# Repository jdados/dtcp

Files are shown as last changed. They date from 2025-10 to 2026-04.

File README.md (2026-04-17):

# CpE Design: DTCP Project Repository

## Overview

This repository presents the files associated with the design of a wireless neurostimulation platform powered through **Differential Tissue Coupled Powering (DTCP)**.  
The system transmits high-frequency (~20 – 25 MHz) differential signals through needle electrodes to power and communicate with implanted devices, while simultaneously recording **EMG (Electromyography)** activity for research.

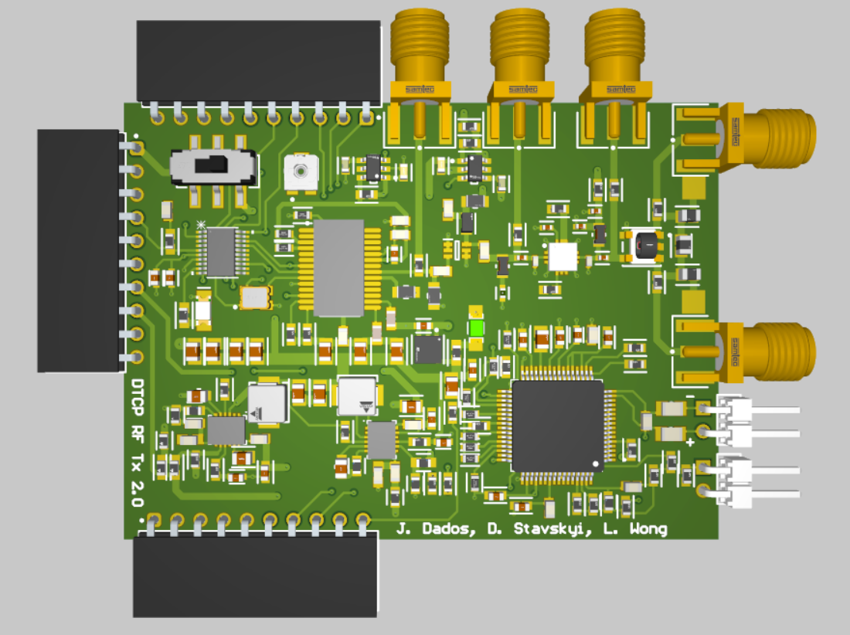
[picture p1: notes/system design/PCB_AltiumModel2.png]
Prototype 2 3D render


The project integrates four key subsystems:

1. **RF Signal Generation** – AD9850 DDS digitally tunes the HF output frequency.  
2. **Power Amplification** – 2 PAs in series deliver ≥ 1 W (≈ 30–35 dBm). Adjustable power through the help of a potentiometer and LED is included to make tuning power in surgery easier. It will light up when EMG signal is detected. 
3. **Signal Acquisition** – ADS1299 AFE captures and amplifies EMG signals.  
4. **Control & Interface** – MSPM0C1104 microcontroller manages DDS control, AFE sampling, and power switching.

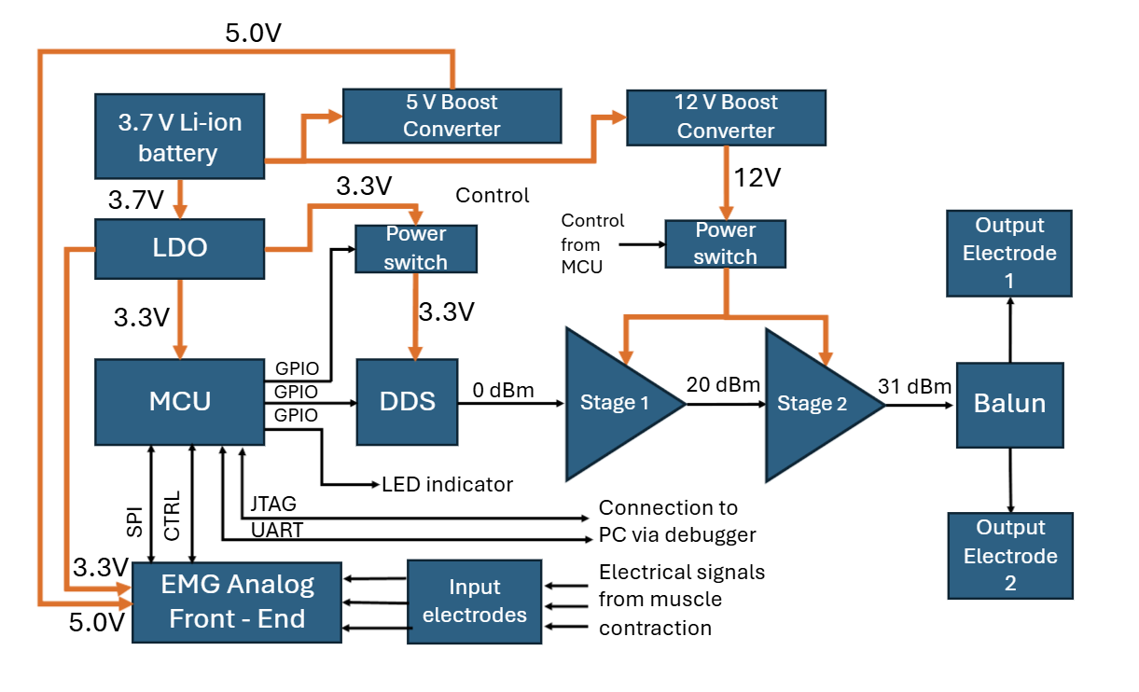
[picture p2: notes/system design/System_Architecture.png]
Prototype 2 System Architecture


## Project Plan

### **First Prototype**

The first prototype aims to realize the most basic functionality: a 25 MHz differential output at 1 W.

| Task | Finish By | Leader | Supporters | Comments | Status |
|------|------------|---------|-------------|-----------|---------|
| Design the PA circuit | End of October 2025 | Luis Wong | Jeremiah Dados |  | ✔️ |
| Design the EMG circuit | End of October 2025 | Dmytro Stavskyi | Jeremiah Dados |  | ✔️ |
| Design the first prototype PCB in Altium | Mid-November 2025 | Jeremiah Dados | Luis Wong, Dmytro Stavskyi |  | ✔️ |
| Place the fabrication order | Mid-November 2025 | Jeremiah Dados | Han Wu |  | ✔️ |
| Receive the board and assemble it | End of November 2025 | Jeremiah Dados | Luis Wong, Dmytro Stavskyi |  | ✔️ |
| Validate board outputs on lab equipment | Mid-December 2025 | Jeremiah Dados | Luis Wong, Dmytro Stavskyi | Present functional prototype at end of semester | ✔️ |
| Validate board functionality in animal experiments | End of January 2026 | Han Wu | Jeremiah Dados, Luis Wong, Dmytro Stavskyi | Work resumes 2nd week of January after winter break | 🟡 |

---

### **Second Prototype**

The second prototype addresses issues found in the first design and focuses on improving compactness, flexibility, and performance.

| Task | Finish By | Leader | Supporters | Comments | Status |
|------|------------|---------|-------------|-----------|---------|
| Revisions to the circuit design | Mid-February 2026 | Luis Wong, Dmytro Stavskyi | Jeremiah Dados |  | ✔️ |
| Design and order the PCB | End of February 2026 | Jeremiah Dados | Luis Wong, Dmytro Stavskyi |  | ✔️ |
| Place the fabrication order | End of February 2026 | Jeremiah Dados | Han Wu |  | ✔️ |
| Receive the board and assemble it | Mid-March 2026 | Luis Wong, Dmytro Stavskyi | Jeremiah Dados |  | ✔️ |
| Validate board outputs on lab equipment | End of March 2026 | Jeremiah Dados | Luis Wong, Dmytro Stavskyi |  | ✔️ |
| Validate board functionality in animal experiments | End of April 2026 | Han Wu | Jeremiah Dados, Luis Wong, Dmytro Stavskyi |  | 🟡 |

## Bugs

### Firmware

- `printf` is apparently too large to fit into the MCU, and debugging is harder without console printing
  - look for smaller alternative, UART cannot be used as it is utilized for EMG plotting through SerialPlot.
- Not yet sure if it causes or will cause problems, but the serial clock starts at high and remains high until the first transaction, even though it should be low when not transmitting or receiving data (and hence should start with low)
  - It has not seemed to though.
- Fluctuating offset, possibly due to noise from main, makes EMG detection algorithm non-trivial.

### Hardware

#### EMG Circuit

- Class A PA is part of the second prototype and maxes out at 31 dBm meeting our target, but when we connect the SMA connector while also recording EMG we seem to face some interference or noise. Perhaps it's due to improper grounding?
- New PCB seems to have introduce more noise causing the EMG + Stimulation signal to be less clean.
  - Something might be shorted.

#### Class E PA

- Due to low Q of inductors the power efficiency we see in simulations is ~30% instead of the >50% we wish for and expect.
- Impedance matching network of Class-E PA might be unoptimized introducing unwanted reactance at output.
- Initial testing shows an extremely weak output signal at -45 dBm.
- Fixing drain inductance yields a power output of 7.26 dBm which is short of the 30dBm target.
- Simulations of the current setup on the physical board show the gain is below what we expected since the gate charge is too high requiring the power at input to be 0.704 W when we are aiming for a 1W output.
  - The current transistor is insufficient for our purposes as it's gate charge is too high to be efficient for amplification to 1W.
- We have elected to drop this design.

## Links

Some files may require UF sign-in:

- [Time Tracking Log](https://docs.google.com/spreadsheets/d/18YieW_wAob6iDCQWRSr79hOXjbCugq7RjKLDexqUogo/edit?gid=0#gid=0)

- [Design Draft](https://docs.google.com/document/d/1d00vnsQUVDlf2uW5-OWDDMQm1jWjiy-7jFtAZofUm3A/edit?tab=t.0)

- [Pre-Alpha Build](https://docs.google.com/document/d/1ijc-FFz9Bt2qVDn8euLwuQjNTMDzeiQRgQFuhg-fLZ0/edit?tab=t.0)

- [Design Prototype](https://docs.google.com/document/d/1iM8SsOxejECSPiFp-hwhw81iVYtYDDtyBoNlvvrWGng/edit?usp=sharing)

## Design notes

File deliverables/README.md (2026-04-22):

# Deliverables

Files associated with CpE Design 1 (CEN4907C) and CpE Design 2 (CEN4908C) course. These are the documents and presentations made to be submitted to the class on canvas.

Below are the order we turned these files in:

## Semester 1 

1. Design Draft
2. Design Plan (Updated version of Design Draft)
3. Pre-Alpha Build
4. Design Prototype 
5. Prototype Presentation

## Semester 2

1. Alpha Build
2. Alpha Test Plan
3. Beta Build
4. Beta Test Plan
5. Beta Presentation
6. Preliminary Report
7. Release Candidate
8. Final Report
9. Final Presentation
10. Production Release

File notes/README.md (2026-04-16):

# Notes

Miscellaneous documents and notes reguarding the design of the device.

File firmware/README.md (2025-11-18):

Tested on Code Composer Studio (CCS) version 20.3.1
Include the during CCS installation
In case it is already installed without that component, you can repeat the installation on the same installation directory

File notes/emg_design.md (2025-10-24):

# General

- ports (connections):
	- ground
	- vdd
	- channel
	- SPI

- components:
	- amplifiers (?)
	- filters (?)

- chip: ADS1299
	- not a microcontroller (external programming using SPI)
	- SPI interface
	- provides amplification
	- can provide low-pass filtering
- use the MCU of the design, MSPM0C1104, to program the ADS1299

- EMG signal characteristics:
	- frequency range: 0 - 500 Hz
	- amplitude range: 0 - 10 mV
	- usual amplification is in the hundreds

- ADS1299 specs:
	- 7.5 electrical characteristics (explain everything: importance of input capacitance, etc.)
	- e.g., if amplitude of EMG is 1 mV, then we need minimum of 16 bit ADC
- SPI: 
	- can fully setup and control the device with SPI (commands include: WAKEUP, STANDBY, START, STOP)
- PGA:
	- gain of up to 24x
- filtering: 
	- external band-pass of 500 Hz and low-pass filters
- ADC: 
	- resolution: 24 bits (assuming reference of 4.5 V, (4.5 V / 2^24^) = 0.268 μV)
	- sampling (data) rate: from 250 SPS to 16 kSPS (~1000 SPS is good?)

- papers using ADS1299:
	- [Development of an 8 channel sEMG wireless device based on ADS1299 with Virtual Instrumentation](https://arxiv.org/abs/1808.03711)
	- [Analog front-ends comparison in the way of a portable, low-power and low-cost EMG controller based on pattern recognition](https://ieeexplore.ieee.org/abstract/document/7318805)
	- [Data acquisition system of 16-channel EEG based on ATSAM3X8E ARM Cortex-M3 32-bit microcontroller and ADS1299 ](https://pubs.aip.org/aip/acp/article/1862/1/030149/649943/Data-acquisition-system-of-16-channel-EEG-based-on)

# Pre-alpha build

- schematic (altium):

- electrodes:
	- how electrodes work (drawings)
	- refer to some paper

- every connection needs to be able to be debugged
- MCU needs to have a launchpad (for debugging; launchpad contains a debugger chip and the chip identical to one used in PCB)

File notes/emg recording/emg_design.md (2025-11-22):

# General

- ports (connections):
	- ground
	- vdd
	- channel
	- SPI

- components:
	- amplifiers (?)
	- filters (?)

- chip: ADS1299
	- not a microcontroller (external programming using SPI)
	- SPI interface
	- provides amplification
	- can provide low-pass filtering
- use the MCU of the design, MSPM0C1104, to program the ADS1299

- EMG signal characteristics:
	- [Myoelectric Interfaces and Related Applications: Current State of EMG Signal Processing–A Systematic Review](https://ieeexplore.ieee.org/document/8949764)
	- frequency range: 0 - 500 Hz
	- amplitude range: 0 - 10 mV
	- usual amplification is apparently in the hundreds

- ADS1299 specs:
	- 7.5 electrical characteristics (explain everything: importance of input capacitance, etc.)
	- e.g., if amplitude of EMG is 1 mV, then we need minimum of 16 bit ADC
- PGA:
	- gain of up to 24x
	- amplifier gain is inversely proportial to the amplifier bandwidth
- filtering: 
	- external band-pass of 10 to 500 Hz
- ADC: 
	- resolution: 24 bits (assuming reference of 4.5 V, (4.5 V / 2^24^) = 0.268 μV)
	- sampling (data) rate: from 250 SPS to 16 kSPS (assuming that 500 Hz is the top limit of the signal, the sampling rate should be at least 1000 SPS to avoid aliasing)

- papers using ADS1299:
	- [Development of an 8 channel sEMG wireless device based on ADS1299 with Virtual Instrumentation](https://arxiv.org/abs/1808.03711)
	- [Analog front-ends comparison in the way of a portable, low-power and low-cost EMG controller based on pattern recognition](https://ieeexplore.ieee.org/abstract/document/7318805)
	- [Data acquisition system of 16-channel EEG based on ATSAM3X8E ARM Cortex-M3 32-bit microcontroller and ADS1299 ](https://pubs.aip.org/aip/acp/article/1862/1/030149/649943/Data-acquisition-system-of-16-channel-EEG-based-on)
	- [Design of low-noise multi-channel active surface electromyography acquisition equipment](https://ieeexplore.ieee.org/abstract/document/10071075)

# Pre-alpha build

- schematic (altium)

- electrodes

- every connection needs to be able to be debugged
- MCU needs to have a launchpad (for debugging; launchpad contains a debugger chip and the chip identical to one used in PCB)

# SPI

## ADS1299

- can fully setup and control the device with SPI (commands include: WAKEUP, STANDBY, START, STOP)
- maximum serial clock frequency of 20 MHz
- uses SPI Mode 1
	- clock polarity: 0 (clock low when not transmiting data)
	- clock phase: 1 (sample at the second clock edge; falling clock edge)
- timing

## MCU

- maximum serial clock frequency is 12 MHz

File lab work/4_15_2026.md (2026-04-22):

# 04/15/2026

Attendees: Dmytro, Luis, Jeremiah, Han

Hours: 7pm - 10pm

## Results

### UART Firmware (Dmytro, Luis, Jeremiah, Han)

- On PCB we tested AGND is shorted to the DGND even with no power, but we do not have the 0 ohm so we need to investigate later what happened there.
- 1st setup PCB was connected to the PSU and it can record EMG, we observed 60 Hz noise which is too large as it overlaps with the signal.
- We started testing with battery, 7:57 is when we took note of the time (3.725V) but the battery has already been running for 5-10mins.
- 60 Hz becomes very small or ignorable and the EMG signal becomes clear.
- We connected the DGND through RF coax cable to oscilloscope ground
- Offset seems to overflow to + or - 185 mV.
- We connected the DGND through RF coax cable to AGND on-board but nothing happens [so it's still working].
- Have an image of setup may link it here once it is uploaded to document changes.
- Will add 1Mohm resistor to replace the 0 ohm at bias and connect bias that was previously connected to the negative terminal to it's own terminal.
    - To make it clear 1 Mohm goes out to bias electrode, and the 0 Ohm that bridged this to negative terminal is now removed so bias is now it's own terminal.
- We need to remove the charger off the PC as it seems to introduce noise.
- Bias is floating.
    - When o-scope (earth ground) is connected to PCB we observe offset near 0 and signal works.
    - When o-scope is disconnected we see lots of noise, enough to drown out the signal.
- Bias in saline.
    - Now with bias in saline, o-scope disconnected makes readable measurements.
    - O-scope connected causes offset to shift, but the signal is still readable.
- We reconnected 0 ohm resistor connecting bias to - electrode. 
    - Make's reasonable measurements with good enough SNR, less electrodes makes this ideal for rat experiments.
- ALL GNDS are connected AGND, DGND, PGND. We cant connect DGND-> EARTH_GND.
- Now it's 8:49 and we detect 3.646 V.
- After testing each stage of the power amplifier we found that the stage 2 chip was damaged, we are replacing it to see if we can get the 31 dBm result we saw previously. This testing is now running in paralell to EMG recording.
- Now after replacing the second stage PA we read 25.2 dBm short of the 31 dBm we had last time, but we do have the BALUN connected now.

## Next Steps

- We will try to measure the power coming out of the BALUN to check if it's where the power loss occurs.

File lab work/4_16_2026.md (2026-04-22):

# 04/16/2026

Attendees: Dmytro, Luis, Jeremiah, Han

Hours: 7pm - 10pm

## Results

### UART Firmware/Hardware (Dmytro, Luis, Jeremiah, Han)

- Seems like something broke in the PA part of the setup and/or board.
- Managed to partially fix it to output 25 dBm once again and will leave it there for the upcoming demo the following Monday and Tuesday.
- Still have yet to develop and implement the EMG detection algorithm.
- Installed the SMA port for the BALUN.
- Current setup shows no noise so long as we are grounded externally, in this case to the oscilloscope via our SMA ports.
- Without this when we disconnect from oscilloscope we experience a lot of noise, with it plugged in we experience no noise or offset drift making this a very stable enviroment to develop the algorithm.

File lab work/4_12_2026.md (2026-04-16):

# 04/12/2026

Attendees: Dmytro, Luis

Hours: 3pm - 5:30pm

## Results

### UART Firmware (Dmytro and Luis)

- Tested new PCB again but powered it through the Launchpad instead of a seperate PSU in the hopes that it would reduce or eliminate the noise we are seeing.
- There does seem to be some improvement but it's still too noisy to develop the detection algorithm or visually make out the EMG signal that follows the stimulation artifact.
    - Our last prototype did not have this issue, we believe it may either be a grounding issue, setup 2 (+ and - electrodes with bias connected to - terminal) is insufficient as opposed to setup 4 (bias, + and - electrodes), or we need to resolder the RC filter (capacitor) at the + and - terminals.

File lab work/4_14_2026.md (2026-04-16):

# 04/14/2026

Attendees: Dmytro, Luis

Hours: 5pm - 8:20pm

Attendees: Dmytro, Luis, Jeremiah

Hours: 8:20pm - 

## Results

### UART Firmware (Dmytro and Luis)

- Retested setup 2 on new PCB but managed to get the interrupts + FIFO for the SPI and UART communication working allowing the MCU more breathing room. 
    - This will enable us to develop the algorithm without impacting transmission.
    - The tradeoff is that to get interrupt based UART TX working we needed to remove the header byte which causes some QOL issues for the user. They will need to skip bytes until SerialPlot is synchronized with the MCU.
- After removing the floating SMA cable, changing the placement of the electrodes relative to the signal generator, and zooming out on our plot we were able to produce a somewhat cleaner result perhaps still a bit worse than the last prototype.
- We recorded a demonstration of plugging in power into the laptop effecting the offset, causing overflow.

### PCB Hardware (Dmytro, Luis, and Jeremiah)
- Removed capacitor and resistor connected to bias and replaced them with 0 ohm.
- Noticed that connected SMA connector to oscilloscope with no attenuator still causes distortion to EMG recording.

#### In an effort to fix this and the noise issue with EMG recording we:
- Resoldered analog ground to digital ground as it was previously floating.
    - The EMG recording is underflowing.
- Test to see if analog grounding pin or bias pin in saline improve EMG recording.
    - No improvement
- Test to see if jumping ground and bias fixes it.
    - No improvement
- Added the capacitor connecting + and - terminals again.
    - No improvement
- Connecting analog or digital ground to saline causes EMG recording to break (possibly means the grounds or shorted elsewhere on the board).
- Resoldered ADS1299 perhaps certain pins were shorting as we had to solder the delicate and finnicky component by hand without a stencil.
    - Tested to see if ADS1299 was functional, it was not.
- Resoldered the ADS1299 again.
- Try multiple times short still persists it seems. May need to wait for assembled version from manufacturer to arrive.

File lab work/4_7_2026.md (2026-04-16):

# 04/07/2026

Attendees: Dmytro, Luis

Hours: 5:30pm - 8:30pm

## Results

### UART Firmware (Dmytro and Luis)

- Tested setup 2 on new board with saline and directly from function generator.
- Had issues initially but they were resolved when we found out we mislabled the negative and positive terminals on the device.
- After swapping we get better readings.
- Tried testing PA + AFE.
    - PA does not output correct power (-18dbm).
    - AFE does not record correctly.
- Found out that when we connected the device to the spectrum analyzer to read power output it causes AFE to read noise, once disconnected the device seems to measure voltage correctly once again. This could be due to a grounding issue.
- There may be an issue with how we activate the PA so we will code review with Jeremiah in the coming days.

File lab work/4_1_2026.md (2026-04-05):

# 04/01/2026

Attendees: Jeremiah

Hours: 4pm - 10pm

## Results

Assembled the RF circuit on the freshly arrived PCB. Took longer than expected because the manufacturer didnt ship the stencil. RF output verified to be 31 dBm. PA drain voltage reduced to 12 V for better stability, no decrease in output power. First stage PA output power measured to be 22 dBm after using an actual RF drain inductor instead of the one suggested by datasheet. First stage PA drain resistor changed to 82 ohm.

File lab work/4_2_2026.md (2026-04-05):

# 04/02/2026

Attendees: Dmytro, Luis

Hours: 1:30pm - 4:00pm

Attendees: Dmytro, Luis, Jeremiah

Hours: 5pm - 9pm

## Results

### UART Firmware (Dmytro and Luis)

- Changed the container we used to store saline to a larger tub about the size of a rat to better mimic use-case.
- Moved bias electrode to other side of dish near the bottom.
- Other electrodes were at the top of the dish.
- Determined that header byte works correctly and mimics previous stable behavior.
- Tried using EMG signal Han provided but testing with both our board and a oscilloscope show signal being strange.
- Attempted to write stimulation artifact detection but noticed it caused issues with UART Tx.
- Determined it was because we were using polling (blocking/busy wait) causing the CPU to be too busy. It disallows the CPU from doing anything but UART Tx.
- Wrote the beginning of UART Interrupt+FIFO based Tx.
- Confirmed it works on standalone UART code, will integrate into AFE code tomorrow.

### AFE Hardware (Jerimiah)

- Soldered Power Tx part of the new board that arrived.

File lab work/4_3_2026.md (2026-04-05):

# 04/03/2026

Attendees: Dmytro, Luis

Hours: 1:30pm - 4pm

## Results

### UART Firmware (Dmytro and Luis)

- Integrated UART Interrupt + FIFO Tx code into AFE code.
  - Noticed some data loss in graph.
- Determined it is due to synchronization issues between AFE and UART.
  - May be fixed if we implement a semaphore?

### AFE Hardware (Jerimiah)

- Progressed more on soldering the new board.

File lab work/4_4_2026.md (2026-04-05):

# 04/04/2026

Attendees: Jeremiah

Hours: 4pm - 10pm

## Results

### AFE Hardware (Jerimiah)

Assembled the power circuits. Had to change the resistors in the 5V boost to (270k || 430k) / (82k || 150k) to produce 5.00 V rather than 6.4 V which was previously there with original resistors.

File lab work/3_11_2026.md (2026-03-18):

# 03/11/2026

Attendees: Dmytro, Luis

Hours: 5pm - 9:30pm

Attendees: Dmytro, Luis, Jeremiah

Hours: 8pm - 9pm

## Results

### UART Firmware (Dmytro and Luis)

- Experimentally testing UART data transmission and plotting using SerialPlot.
- Used MATLAB to generate a test signal at 100Hz 2.5Vdd sampled at 1kHz.
- Wrote code to transmit data as raw binary data on top of sending it as ASCII as we have been doing before.
  - No spiking occures when just using launchpad to transmit data.
  - Both ASCII and binary seem to work with binary having syncing issues, may need a header byte.
- Tested ASCII code.
  - MCU + ADS1299 spiking in plot occurs.
  - 115200 baud rate fixes spiking, reoccurs when we change the amplitude of the signal.
  - Adding parity bit and stop bits does not fix issue.
- Attempted to use SRB1, but some issues occured.
  - The measured data saturates (to -187.5 mV) when it should not saturate.
- Can read the analog data from channel 2.
- The spiking issue appears when measuring data with saline.
- Need to test whether the spiking is an UART issue or whether those spikes are actual data points but the CCS graph did not capture them

### AFE Hardware (Dmytro, Luis, Jerimiah)

- Soldered SMDs for channel 2 of AFE.
	- Added filter for channel 2 of AFE.
- Shorted bias pins with SRB1.

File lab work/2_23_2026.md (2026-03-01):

- Time: 8pm - 11pm
- Attendees: Jeremiah

The second stage PA still outputs lower power. I noticed that the solder paste I've been using produces really poor bonds, which could explain the unexpected issues with the circuit. Stable performance was achieved after removing that solder paste from the board and re-soldering with better, new solder paste.

- Time: 12:30pm - 2:30pm
- Attendees: Dmytro

- I focused on improving the existing code changing things one by one and seeing whether it would break the behavior or not
    - moved most of the main into functions inside the ADS1299 header / source files
    - also changed the code so that it does SPI commands for things like reset instead of pin pulling, so we release those pins from MCU for GPIO

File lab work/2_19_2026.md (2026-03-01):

- Time: 8pm - 11pm
- Attendees: Jeremiah

The second stage PA still outputs lower power. Any attempts to fix it completely break the circuit.

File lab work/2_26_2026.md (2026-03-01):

- Time: 7pm - 11pm
- Attendees: Jeremiah

I verified that 1ms pulsed transmission can be achieved using the power switches, and it reduces the static current to < 1mA.

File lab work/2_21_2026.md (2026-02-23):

# 01/27/2026

Attendees: Jeremiah, Luis, Dmytro

Hours: 5:00pm - 8:00pm

## Results

### Firmware (Dmytro)

- Changed the setup so now there is a saline solution to mimic a biomedical setup
- Can measure the signal when the positive terminal of the input channel is connected to the signal from the function generator via saline, but there is an offset and it's not constant
	- digital filtering to remove the offset
- When computing FFT of the measured signal, there is a much greater DC component than before
- When measuring the signal with everything (the terminals of the input channel and the signal generator terminals) shorted via saline, there seems to be signal but it's not consistent

### Firmware (Luis)
- Got familiar with the LaunchPad MSPM0C1104 and CCS.
- Wrote firmware that transmitted from the MCU an array of floats to console on the PC through UART.
- This should allow the device to send data to a computer.

### Hardware (Jeremiah)

- Was able to get the whole system working, but at lower power. After re-soldering the second stage PA, it stopped working.

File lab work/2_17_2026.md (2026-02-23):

- Time: 7pm - 11pm
- Attendees: Jeremiah

I was finally able to get the complete system to work. The issue was that the 100 MHz crystal used by the DDS was damaged from heat, and therefore there was no RF output at all. However, after fixing the crystal, the output power is less than before, at only 28.6 dBm.

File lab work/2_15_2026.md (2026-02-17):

- Time: 2pm - 5:30pm
- Attendees: Dmytro, Jeremiah

- Tested ways to offset an external analog signal (AFE)
    - can, in a way, offset a 0V DC signal (generated by the function generator) by 2.5V using a power supply (connect the positive terminal of the power supply to the ground terminal of the signal; measured using DAD oscilloscope)
    - can measure the normal input signals using a bias (somehow it works)
    - right now, all bias signals (biasin, biasnv, and biasout) are shorted and are connected to the ground terminal of the input signal and to the negative terminal of the channel (so the signal is offset by 2.5V and the negative terminal is 2.5V)
    - in principle, if the reference or the bias electrode is equivalent to the ground of all the electrodes, connecting it to the 2.5V (e.g., generated by bias) will offset all the electrodes (if this is the setup)

Hardware:
- Continued trying to assemble to full system PCB. The DDS circuit produced no output, and it was behaving abnormally as evidenced by fluctuating current consumption.

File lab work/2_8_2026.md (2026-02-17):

# 02/08/2026

Attendees: Jeremiah, Luis, Dmytro

Hours: 8:00pm - 9:00pm

## Results

### Firmware (Dmytro and Luis)

- Can properly measure both the differential and single-ended normal inputs from the function generator when offset by 2.5V DC
- Now we can properly graph the values with the CCS Graph functionality and apply FFT to see the frequencies
- Tested the internal bias drive amplifier by shorting the outputs and inputs, but it seems it does not correctly with our current circuit
- Can send a string to the PC over UART for potential data plotting
  - no function for sending and receiving floating numbers yet
  - can potentially use Python with PySerial

### Hardware (Jeremiah)

- Attempted to build a complete system on one PCB, but was unable to get the DDS circuit to work after moving it to a new PCB.

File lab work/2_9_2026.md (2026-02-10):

Time: 6pm - 8pm
Attendees: Jeremiah

Continued trying to get the complete PCB to work. the DDS circuit worked periodically but was unstable, and by the end of the session returned back to not working.

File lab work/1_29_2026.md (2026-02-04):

# 01/29/2026

Attendees: Jeremiah, Luis, Dmytro

Hours: 8:00pm - 9:00pm

## Results

### Firmware (Dmytro)

- Adding more delay fixed the RESET command so now it works correctly and the circuit works at the first time without reflashing
- By creating the internal test signal and routing the channel 1 input to that instead of the normal external terminals (by configuring MUXes), we can properly measure it
	- we can assume that the current implementation of data capture is correct, since we can correctly output the internal 1.875mV square wave
- For the normal input to the channel, we are measuring values near zero (~0.019 mV) that do not change except as the amplitude increases at high voltages (in the range of Volts), where we do get some mV (1-3)
	- might be a grounding issue

### Hardware (Luis and Jeremiah)

#### Class-E

- Made a model in LTspice to mimic the setup we have on the board, the new file is called `Class_E_TB.asc`.

#### Power Switches

- Testing the power switches on the DDS.
- The power switch can completely diconnect and reconect the DDS and the current when disconnected is less than 1mA.

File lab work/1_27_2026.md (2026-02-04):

# 01/27/2026

Attendees: Jeremiah, Luis, Dmytro

Hours: 1:00pm - 3:00pm

Atendees: Dmytro

Hours: 5:00pm - 8:00pm

## Results

Today, we continued the work on AFE firmware.
We also determined the performance of the class-E circuit. It delivers up to 13.5 dBm at 20 MHz and 7.5 dBm at 25 MHz, while consuming 1.37 A of current.

### Firmware (Dmytro)

- Fixed timing issues with the SPI such that we can can send SPI commands like START and they can be properly decoded
- Fixed the issues with the RX buffer so now we can properly read both the registers with the first time and the analog data overall
	- the analog data measured from the normal inputs seem to be just noise

### Hardware (Luis and Jeremiah)

#### Class-E

- At drain we have the same 1.5 uH inductor as before made use of four total with 2 pairs of them in series then connected in parallel. 
- At 25 MHz after this change we are now getting 7.26 dBm instead of the negative 40 dBm we got before using a 0-4.5V square wave.
- When the signal at the gate is modified to a 0 to 4 V square wavewith 3.3V or 5V at drain we get about negative 2 dBm. 
- We seem to be getting the best results in terms of power output using a 0V - 4.5V square wave.
- When sweeping frequencies, it becomes evident that the power output of the device peaks at around 18-20 MHz.
- Without changing the setup of using 3.7V at drain and a 0-4.5V squarewave at the PA gave 13.5 dBm at 20 MHz.
- After increasing the drain voltage to 5V we saw that the signal amplified further to 15dBm but we had to stop there as we were worried we would damage the SMAs if we continued.

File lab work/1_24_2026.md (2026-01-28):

# 01/24/2026

Attendees: Jeremiah, Luis, Dmytro

Hours: 5:30pm - 8:00pm

## Results

For the firmware side, we managed to get the data ready signal to work and now should be able to get the conversion data.

### Firmware (Dmytro)

- After making the reset pin not floating (amongs other changes), the data ready signal now transitions from high (false) to low (true)
  - it seems to behave normally, e.g., if START pin is not high, DRDY (active low) signal stays high (which is the intended behavior; not tested with START command)
- Only tested once, but it seems we get a non-zero data with the shorted analog channels (which may be the status register bits or the way the data is captured is incorrect)
- The analog part also draws 4 mA

### Hardware (Luis and Jeremiah)

#### Class-E

- We realized we forgot to resolder a resistor going our of the PA which led to not getting any output.
- We will need to revisit this PA later.

#### Class-A

Both PA1 and PA2 using 12V:

- At 68 ohms of drain resistance we get 28.4 dBm. 
- At 51 ohms at the drain the current consumption is 340mA and the output power is 29.7 dBm.

Both PA1 and PA2 using 12.5V:

- At 51 ohms at the drain the current consumption is 360mA and output power is 30.3 dBm.

Both PA1 and PA2 using 13V:

- At 51 ohms at the drain the current consumption is 380mA and output power is 30.7 dBm.

- Installed BALUN and SMA connectors.
- Using differential outputs: One of the outputs is 26 dBm at 13V with the other output open.
- The same is true at the other output with no load on the other.

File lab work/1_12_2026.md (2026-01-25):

# 01/12/2026

Attendees: Jeremiah

## Results

Today, I assembled the MCU, DDS, and class-A PA1 circuits. The MCU circuit is fully functional. The DDS circuit is fully functional (except for the potentiometer that sometimes mechanically fails) and outputs 0 dBm. However, the gain of PA1 is really low, outputting only 3.5 dBm with the 0dBm input from DDS.

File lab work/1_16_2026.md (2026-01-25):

# 01/24/2026

Attendees: Jeremiah, Dmytro

Hours: 6pm - 10pm

## Results

Today, me and Dmytro went to the lab to assemble a version of the circuit for firmware development.

- Assembled a circuit consisting of an MSP evaluation board and our AFE chip on an empty PCB, with the two chips connected through jumper wires, with SPI lines connected to an oscilloscope and power supplied from a lab DC source
- We were able to output correct numbers through SPI, but we learned the SPI driver pulls CS high between each transaction, which is not acceptable for our AFE chip.
- Because of that, nothing was showing up on MISO.
- Next steps: adjust firmware so we can communicate with the AFE and read back data.

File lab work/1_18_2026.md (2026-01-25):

# 01/18/2026

Attendees: Jermiah, Dmytro, Luis

Hours: 3pm - 6pm

## Results

Today, we met as a group in the lab to continue working on the firmware and the power amplifier.

### Firmware (Dmytro and Jerimiah)

- We made the CS a GPIO pin in order to have more control over it, specifically in order to have valid SPI transactions as defined by the datasheet for the chip, and now can properly pull down and pull up the pin.
- We were able to get 0.034 A (instead of 0.01 ~ 0 A initially) to be output by the chip, indicating that the chip is actually powered up.
- With the current code, we also get data from MISO and can now properly read from registers (for now, only tested with reset values).

### Hardware (Luis and Jerimiah)

- We constructed a test circuit on a separate board for the class-E amplifier.
- Our current goal as we wait for the pre-built PA chip to arrive is to confirm the design outputs at close to 30dBm.
- We made use of parts on hand to approximate the values for the capicitors and inductors used in simuluation.
  - Drain inductor used was 1.5 uH.
  - Approximated 120 pF to 112pF using two 56pF capacitors in parallel.
  - Approximated a 120nH and 85nH in series with two 68nH and two 39nH inductors in series.

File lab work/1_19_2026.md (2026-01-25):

# 01/19/2026

Attendees: Jeremiah, Luis, Dmytro

Hours: 6pm - 9pm

## Results

Today,  ran the first tests on the class-E PA circuit we constructed earlier. The input to the gate was provided from a signal generator (a 0V-3.3V square wave at 25 MHz), the drain voltage was supplied from a DC power supply (3.7V), and the output was connected to a spectrum analyzer. After turning on the gate signal, the drain current increased to 30mA - 700mA as the amplitude was gradually increased. However, the output signal was extremely weak, at -45 dBm.

## Next Steps

Analyze if the component changes we made could've caused the signal to be this attenuated.

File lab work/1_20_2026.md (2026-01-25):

# 01/20/2026

Attendees: Jeremiah

## Results

Today, I assembled the full class-A RF signal chain (DDS + PA1 + PA2). PA2 was placed on a separate board as the PA2 area on the board with PA1 and DDS became damaged in the process of testing. The full circuit produced 27.7 dBm at 25MHz with PA1_VDD = 5.0 V and PA2_VDD = 12.0V. 29.5 dBm was achieved after increasing PA1_VDD to 7.0V. Then 30.0 dBm was achieved after increasing PA2_VDD to 12.5 V.

## Next Steps

Change the resistor in PA1 circuit to allow for 12V VDD in both devices.

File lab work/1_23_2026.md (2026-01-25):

# 01/23/2026

Attendees: Jeremiah, Luis, Dmytro

Hours: 6pm - 8:30pm

## Results

Today, we tested changing the supply voltage of the 1st stage class-A PA and seeing how it affects the output.
We also tried sweeping different gate signal frequencies for the class-E circuit to see if the resonant frequency is not 25 MHz.

### Firmware (Dmytro)

- Tested different operations like transmitting a command and reading a register in the form of functions
	- some work if directly embedded into the main but not as a function
- Still unable to receive conversion data from the analog channel
	- even though we are sending a START and RDATAC (read data continuously) commands, DRDY (data ready) pin is never asserted
	- same problem even when using a single-shot mode

### Hardware (Luis and Jerimiah)

#### Class-E

- We were tasked to sweep frequencies to find whether or not the resonant frequency was 25MHz.
  - Might not be possible if resonant frequency is above 25MHz due to signal generator only supporting a max frequency if 25MHz.
- After experimenting with the design we were unable to provide any significant amplification and due to time constraints have opted to abandon the class E design.

### Class-A

For PA1:

- At 170 ohms we got 2.2 dBm.
- With 150 ohms we got 2.7 dBm.

Both PA1 and PA2 using 12V:

- 28.7 dBm with 100 ohms.

Changing to 82 ohms:

- 28.2 dBm with 12V
- 28.9 dBm with 13V

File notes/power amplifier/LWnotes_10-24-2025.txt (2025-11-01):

https://oa.upm.es/54834/1/INVE_MEM_2018_297638.pdf
https://people.eecs.berkeley.edu/~culler/AIIT/papers/radio/Sokal%20AACD5-poweramps.pd
https://www.microwavejournal.com/articles/1716-high-efficiency-power-amplifier-driving-methods-and-circuits-part-i
https://www.microwavejournal.com/articles/1672-high-efficiency-power-amplifier-driving-methods-and-circuits-part-ii
https://people.physics.anu.edu.au/~dxt103/160m/class_E_amplifier_design.pdf
https://www.researchgate.net/publication/251836683_Effects_of_the_Sine-Wave_Drive_in_Class-E_Tuned_Power_Amplifiers
https://www.researchgate.net/publication/3450801_Power_Losses_and_Efficiency_of_Class-E_Power_Amplifier_at_Any_Duty_Ratio
https://chic.caltech.edu/wp-content/uploads/2013/05/ZVS.pdf?utm_source=chatgpt.com
https://www.ti.com/lit/ds/symlink/ucc27511.pdf?ts=1761212888929 (Possible Driver)

https://www.ti.com/lit/ds/symlink/ucc27511.pdf?ts=1761212888929
If we go with square waves , which should be possible as the DDS seems to have comparator built in for that purpose, there is this driver available which should be capable of running up to 43MHz.
For our use case of this device a 12V supply voltage is good enough. 
The paper I referenced earlier was written in 2004 but it seems solutions for the problems of HF drivers have appeared more recently.
Square waves are preferred over sine waves when using Class-E amplifiers as we want to reduce the time we are in the saturation region of the MOSFET for efficiency reasons.
Class-E amplifiers unlike other classes of amplifiers need the MOSFET to act like a switch rather than a linear amplifier which is why it prefers square waves over sine waves.
If we do use sine waves we would need to double the Vpp of what we would otherwise use in a square wave which can be a little annoying. 

Need to compare EPC2065 (GaN FET) to the IRF510 (Si MOSFET)

May need a buck to reduce voltage efficiently as GaN FET is driven using a 6Vpp

12V IN

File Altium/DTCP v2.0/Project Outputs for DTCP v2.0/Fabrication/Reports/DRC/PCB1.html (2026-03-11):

Altium

# Design Rule Verification Report

Date: | | 3/5/2026
Time: | | 5:17:23 PM
Elapsed Time: | | 00:00:01
Filename: | | C:\Users\jdado\AppData\Local\TempReleases\Snapshot\1\PCB1.PcbDoc

Warnings: | | 0
Rule Violations: | | 0
Waived Violations: | | 336

## Summary

Warnings | Count
Total | 0

Rule Violations | Count
Clearance Constraint (Gap=10mil) (All),(All) | 0
Short-Circuit Constraint (Allowed=No) (All),(All) | 0
Un-Routed Net Constraint ( (All) ) | 0
Modified Polygon (Allow modified: No), (Allow shelved: No) | 0
Width Constraint (Min=10mil) (Max=80mil) (Preferred=10mil) (All) | 0
Power Plane Connect Rule(Relief Connect )(Expansion=20mil) (Conductor Width=10mil) (Air Gap=10mil) (Entries=4) (All) | 0
Hole Size Constraint (Min=1mil) (Max=100mil) (All) | 0
Hole To Hole Clearance (Gap=10mil) (All),(All) | 0
Minimum Solder Mask Sliver (Gap=10mil) (All),(All) | 0
Silk To Solder Mask (Clearance=10mil) (IsPad),(All) | 0
Silk to Silk (Clearance=10mil) (All),(All) | 0
Net Antennae (Tolerance=0mil) (All) | 0
Height Constraint (Min=0mil) (Max=1000mil) (Prefered=500mil) (All) | 0
Total | 0

Waived Violations | Count
Clearance Constraint (Gap=10mil) (All),(All) | 9
Minimum Solder Mask Sliver (Gap=10mil) (All),(All) | 202
Silk To Solder Mask (Clearance=10mil) (IsPad),(All) | 124
Silk to Silk (Clearance=10mil) (All),(All) | 1
Total | 336

## Rule Violations

## Waived Violations

Clearance Constraint (Gap=10mil) (All),(All)

Clearance Constraint: (6.89mil < 10mil) Between Pad U5-7(4289.012mil,2667.987mil) on Top Layer And Region (0 hole(s)) Top Layer
Waived by Jeremiah Dados at 3/1/2026 3:46:15 PM

Clearance Constraint: (6.89mil < 10mil) Between Pad U5-7(4289.012mil,2667.987mil) on Top Layer And Region (0 hole(s)) Top Layer
Waived by Jeremiah Dados at 3/1/2026 3:46:15 PM

Clearance Constraint: (6.89mil < 10mil) Between Pad U5-7(4289.012mil,2667.987mil) on Top Layer And Region (0 hole(s)) Top Layer
Waived by Jeremiah Dados at 3/1/2026 3:46:15 PM

Clearance Constraint: (6.89mil < 10mil) Between Pad U5-7(4289.012mil,2667.987mil) on Top Layer And Region (0 hole(s)) Top Layer
Waived by Jeremiah Dados at 3/1/2026 3:46:15 PM

Clearance Constraint: (6.89mil < 10mil) Between Pad U5-7(4289.012mil,2667.987mil) on Top Layer And Region (0 hole(s)) Top Layer
Waived by Jeremiah Dados at 3/1/2026 3:46:15 PM

Clearance Constraint: (19.685mil < 20mil) Between Region (0 hole(s)) Top Layer And Region (0 hole(s)) Top Layer
Waived by Jeremiah Dados at 3/1/2026 3:46:15 PM

Clearance Constraint: (19.685mil < 20mil) Between Region (0 hole(s)) Top Layer And Region (0 hole(s)) Top Layer
Waived by Jeremiah Dados at 3/1/2026 3:46:15 PM

Clearance Constraint: (19.63mil < 20mil) Between Region (0 hole(s)) Top Layer And Track (4287.598mil,2616.794mil)(4325mil,2616.794mil) on Top Layer
Waived by Jeremiah Dados at 3/4/2026 3:12:00 PM

Clearance Constraint: (19.681mil < 20mil) Between Region (0 hole(s)) Top Layer And Track (4290.149mil,2721.149mil)(4290.149mil,2775mil) on Top Layer
Waived by Jeremiah Dados at 3/4/2026 3:12:00 PM

Back to top

Minimum Solder Mask Sliver (Gap=10mil) (All),(All)

Minimum Solder Mask Sliver Constraint: (5.904mil < 10mil) Between Pad C19-1(4480mil,2554.782mil) on Top Layer And Pad C19-2(4480mil,2605.218mil) on Top Layer [Top Solder] Mask Sliver [5.904mil]
Waived by Jeremiah Dados at 11/7/2025 11:43:55 PM

Minimum Solder Mask Sliver Constraint: (5.904mil < 10mil) Between Pad C22-1(4715mil,1995mil) on Top Layer And Pad C22-2(4664.565mil,1995mil) on Top Layer [Top Solder] Mask Sliver [5.904mil]
Waived by Jeremiah Dados at 11/7/2025 11:43:55 PM

Minimum Solder Mask Sliver Constraint: (5.779mil < 10mil) Between Pad C23-1(5190.591mil,2080mil) on Top Layer And Pad C23-2(5139.409mil,2080mil) on Top Layer [Top Solder] Mask Sliver [5.779mil]
Waived by Jeremiah Dados at 3/4/2026 3:12:00 PM

Minimum Solder Mask Sliver Constraint: (9.716mil < 10mil) Between Pad C24-1(5225mil,2334.409mil) on Top Layer And Pad C24-2(5225mil,2385.59mil) on Top Layer [Top Solder] Mask Sliver [9.716mil]
Waived by Jeremiah Dados at 11/7/2025 11:43:55 PM

Minimum Solder Mask Sliver Constraint: (5.904mil < 10mil) Between Pad C25-1(5060mil,2694.565mil) on Top Layer And Pad C25-2(5060mil,2745mil) on Top Layer [Top Solder] Mask Sliver [5.904mil]
Waived by Jeremiah Dados at 11/7/2025 11:43:55 PM

Minimum Solder Mask Sliver Constraint: (5.904mil < 10mil) Between Pad C26-1(4605.217mil,2040mil) on Top Layer And Pad C26-2(4554.783mil,2040mil) on Top Layer [Top Solder] Mask Sliver [5.904mil]
Waived by Jeremiah Dados at 11/7/2025 11:43:55 PM

Minimum Solder Mask Sliver Constraint: (5.904mil < 10mil) Between Pad C27-1(4695mil,2684.782mil) on Top Layer And Pad C27-2(4695mil,2735.218mil) on Top Layer [Top Solder] Mask Sliver [5.904mil]
Waived by Jeremiah Dados at 11/7/2025 11:43:55 PM

Minimum Solder Mask Sliver Constraint: (5.904mil < 10mil) Between Pad C31-1(4854.096mil,2695.174mil) on Top Layer And Pad C31-2(4854.096mil,2745.609mil) on Top Layer [Top Solder] Mask Sliver [5.904mil]
Waived by Jeremiah Dados at 11/7/2025 11:43:55 PM

Minimum Solder Mask Sliver Constraint: (9.519mil < 10mil) Between Pad C36-1(4926.334mil,3197.087mil) on Top Layer And Pad C36-2(4960.079mil,3197.087mil) on Top Layer [Top Solder] Mask Sliver [9.519mil]
Waived by Jeremiah Dados at 11/7/2025 11:43:55 PM

Minimum Solder Mask Sliver Constraint: (9.519mil < 10mil) Between Pad C37-1(4783.206mil,3192.087mil) on Top Layer And Pad C37-2(4816.951mil,3192.087mil) on Top Layer [Top Solder] Mask Sliver [9.519mil]
Waived by Jeremiah Dados at 11/7/2025 11:43:55 PM

Minimum Solder Mask Sliver Constraint: (9.519mil < 10mil) Between Pad C38-1(4991.334mil,3262.087mil) on Top Layer And Pad C38-2(5025.079mil,3262.087mil) on Top Layer [Top Solder] Mask Sliver [9.519mil]
Waived by Jeremiah Dados at 11/7/2025 11:43:55 PM

Minimum Solder Mask Sliver Constraint: (9.519mil < 10mil) Between Pad C39-1(4673.206mil,3062.087mil) on Top Layer And Pad C39-2(4706.951mil,3062.087mil) on Top Layer [Top Solder] Mask Sliver [9.519mil]
Waived by Jeremiah Dados at 3/1/2026 3:46:15 PM

Minimum Solder Mask Sliver Constraint: (9.519mil < 10mil) Between Pad C40-1(5023.206mil,3062.087mil) on Top Layer And Pad C40-2(5056.951mil,3062.087mil) on Top Layer [Top Solder] Mask Sliver [9.519mil]
Waived by Jeremiah Dados at 11/7/2025 11:43:55 PM

Minimum Solder Mask Sliver Constraint: (0.662mil < 10mil) Between Pad C41-1(4980.079mil,3031.378mil) on Top Layer And Pad C41-2(4980.079mil,3062.087mil) on Top Layer [Top Solder] Mask Sliver [0.662mil]
Waived by Jeremiah Dados at 11/7/2025 11:43:55 PM

Minimum Solder Mask Sliver Constraint: (0.662mil < 10mil) Between Pad C42-1(4750.079mil,3031.732mil) on Top Layer And Pad C42-2(4750.079mil,3062.441mil) on Top Layer [Top Solder] Mask Sliver [0.662mil]
Waived by Jeremiah Dados at 11/7/2025 11:43:55 PM

Minimum Solder Mask Sliver Constraint: (5.904mil < 10mil) Between Pad C43-1(3590mil,2165.218mil) on Top Layer And Pad C43-2(3590mil,2114.782mil) on Top Layer [Top Solder] Mask Sliver [5.904mil]
Waived by Jeremiah Dados at 3/1/2026 3:46:15 PM

Minimum Solder Mask Sliver Constraint: (9.717mil < 10mil) Between Pad C44-1(3258.425mil,2350mil) on Top Layer And Pad C44-2(3311.575mil,2350mil) on Top Layer [Top Solder] Mask Sliver [9.717mil]
Waived by Jeremiah Dados at 3/1/2026 3:46:15 PM

Minimum Solder Mask Sliver Constraint: (5.904mil < 10mil) Between Pad C7-1(4305mil,2344.782mil) on Top Layer And Pad C7-2(4305mil,2395.218mil) on Top Layer [Top Solder] Mask Sliver [5.904mil]
Waived by Jeremiah Dados at 3/1/2026 3:46:15 PM

Minimum Solder Mask Sliver Constraint: (9.717mil < 10mil) Between Pad C8-1(4147.992mil,2114.291mil) on Top Layer And Pad C8-2(4147.992mil,2167.441mil) on Top Layer [Top Solder] Mask Sliver [9.717mil]
Waived by Jeremiah Dados at 3/1/2026 3:46:15 PM

Minimum Solder Mask Sliver Constraint: (7.769mil < 10mil) Between Pad L14-1(5380mil,2990mil) on Top Layer And Pad L14-2(5433.219mil,2990mil) on Top Layer [Top Solder] Mask Sliver [7.769mil]
Waived by Jeremiah Dados at 11/7/2025 11:43:55 PM

Minimum Solder Mask Sliver Constraint: (7.769mil < 10mil) Between Pad L16-1(5380mil,3141.61mil) on Top Layer And Pad L16-2(5380mil,3088.39mil) on Top Layer [Top Solder] Mask Sliver [7.769mil]
Waived by Jeremiah Dados at 11/7/2025 11:43:55 PM

Minimum Solder Mask Sliver Constraint: (7.769mil < 10mil) Between Pad L17-1(5431.61mil,3240mil) on Top Layer And Pad L17-2(5378.39mil,3240mil) on Top Layer [Top Solder] Mask Sliver [7.769mil]
Waived by Jeremiah Dados at 11/7/2025 11:43:55 PM

Minimum Solder Mask Sliver Constraint: (8.685mil < 10mil) Between Pad U1-1(3318.5mil,3173.583mil) on Top Layer And Pad U1-2(3318.5mil,3153.898mil) on Top Layer [Top Solder] Mask Sliver [8.685mil]
Waived by Jeremiah Dados at 3/4/2026 3:12:00 PM

Minimum Solder Mask Sliver Constraint: (8.685mil < 10mil) Between Pad U1-10(3318.5mil,2996.417mil) on Top Layer And Pad U1-9(3318.5mil,3016.102mil) on Top Layer [Top Solder] Mask Sliver [8.685mil]
Waived by Jeremiah Dados at 3/4/2026 3:12:00 PM

Minimum Solder Mask Sliver Constraint: (1.843mil < 10mil) Between Pad U11-1(3475mil,2378.661mil) on Top Layer And Pad U11-13(3425.787mil,2321.575mil) on Top Layer [Top Solder] Mask Sliver [1.843mil]
Waived by Jeremiah Dados at 3/4/2026 3:12:00 PM

Minimum Solder Mask Sliver Constraint: (1.843mil < 10mil) Between Pad U11-1(3475mil,2378.661mil) on Top Layer And Pad U11-2(3455.315mil,2378.661mil) on Top Layer [Top Solder] Mask Sliver [1.843mil]
Waived by Jeremiah Dados at 3/4/2026 3:12:00 PM

Minimum Solder Mask Sliver Constraint: (5.801mil < 10mil) Between Pad U11-1(3475mil,2378.661mil) on Top Layer And Via (3465.157mil,2341.26mil) from Top Layer to Bottom Layer [Top Solder] Mask Sliver [5.801mil]
Waived by Jeremiah Dados at 3/4/2026 3:12:00 PM

Minimum Solder Mask Sliver Constraint: (8.685mil < 10mil) Between Pad U1-11(3491.5mil,2996.417mil) on Top Layer And Pad U1-12(3491.5mil,3016.102mil) on Top Layer [Top Solder] Mask Sliver [8.685mil]
Waived by Jeremiah Dados at 3/4/2026 3:12:00 PM

Minimum Solder Mask Sliver Constraint: (1.843mil < 10mil) Between Pad U11-10(3435.63mil,2264.488mil) on Top Layer And Pad U11-11(3455.315mil,2264.488mil) on Top Layer [Top Solder] Mask Sliver [1.843mil]
Waived by Jeremiah Dados at 3/4/2026 3:12:00 PM

Minimum Solder Mask Sliver Constraint: (1.843mil < 10mil) Between Pad U11-10(3435.63mil,2264.488mil) on Top Layer And Pad U11-13(3425.787mil,2321.575mil) on Top Layer [Top Solder] Mask Sliver [1.843mil]
Waived by Jeremiah Dados at 3/4/2026 3:12:00 PM

Minimum Solder Mask Sliver Constraint: (1.843mil < 10mil) Between Pad U11-10(3435.63mil,2264.488mil) on Top Layer And Pad U11-9(3415.945mil,2264.488mil) on Top Layer [Top Solder] Mask Sliver [1.843mil]
Waived by Jeremiah Dados at 3/4/2026 3:12:00 PM

Minimum Solder Mask Sliver Constraint: (5.801mil < 10mil) Between Pad U11-10(3435.63mil,2264.488mil) on Top Layer And Via (3425.787mil,2301.89mil) from Top Layer to Bottom Layer [Top Solder] Mask Sliver [5.801mil]
Waived by Jeremiah Dados at 3/4/2026 3:12:00 PM

Minimum Solder Mask Sliver Constraint: (1.843mil < 10mil) Between Pad U11-11(3455.315mil,2264.488mil) on Top Layer And Pad U11-12(3475mil,2264.488mil) on Top Layer [Top Solder] Mask Sliver [1.843mil]
Waived by Jeremiah Dados at 3/4/2026 3:12:00 PM

Minimum Solder Mask Sliver Constraint: (1.843mil < 10mil) Between Pad U11-11(3455.315mil,2264.488mil) on Top Layer And Pad U11-13(3425.787mil,2321.575mil) on Top Layer [Top Solder] Mask Sliver [1.843mil]
Waived by Jeremiah Dados at 3/4/2026 3:12:00 PM

Minimum Solder Mask Sliver Constraint: (5.801mil < 10mil) Between Pad U11-11(3455.315mil,2264.488mil) on Top Layer And Via (3465.157mil,2301.89mil) from Top Layer to Bottom Layer [Top Solder] Mask Sliver [5.801mil]
Waived by Jeremiah Dados at 3/4/2026 3:12:00 PM

Minimum Solder Mask Sliver Constraint: (1.843mil < 10mil) Between Pad U11-12(3475mil,2264.488mil) on Top Layer And Pad U11-13(3425.787mil,2321.575mil) on Top Layer [Top Solder] Mask Sliver [1.843mil]
Waived by Jeremiah Dados at 3/4/2026 3:12:00 PM

Minimum Solder Mask Sliver Constraint: (5.801mil < 10mil) Between Pad U11-12(3475mil,2264.488mil) on Top Layer And Via (3465.157mil,2301.89mil) from Top Layer to Bottom Layer [Top Solder] Mask Sliver [5.801mil]
Waived by Jeremiah Dados at 3/4/2026 3:12:00 PM

Minimum Solder Mask Sliver Constraint: (1.843mil < 10mil) Between Pad U11-13(3425.787mil,2321.575mil) on Top Layer And Pad U11-2(3455.315mil,2378.661mil) on Top Layer [Top Solder] Mask Sliver [1.843mil]
Waived by Jeremiah Dados at 3/4/2026 3:12:00 PM

Minimum Solder Mask Sliver Constraint: (1.843mil < 10mil) Between Pad U11-13(3425.787mil,2321.575mil) on Top Layer And Pad U11-3(3435.63mil,2378.661mil) on Top Layer [Top Solder] Mask Sliver [1.843mil]
Waived by Jeremiah Dados at 3/4/2026 3:12:00 PM

Minimum Solder Mask Sliver Constraint: (1.843mil < 10mil) Between Pad U11-13(3425.787mil,2321.575mil) on Top Layer And Pad U11-4(3415.945mil,2378.661mil) on Top Layer [Top Solder] Mask Sliver [1.843mil]
Waived by Jeremiah Dados at 3/4/2026 3:12:00 PM

Minimum Solder Mask Sliver Constraint: (1.843mil < 10mil) Between Pad U11-13(3425.787mil,2321.575mil) on Top Layer And Pad U11-5(3396.26mil,2378.661mil) on Top Layer [Top Solder] Mask Sliver [1.843mil]
Waived by Jeremiah Dados at 3/4/2026 3:12:00 PM

Minimum Solder Mask Sliver Constraint: (1.843mil < 10mil) Between Pad U11-13(3425.787mil,2321.575mil) on Top Layer And Pad U11-6(3376.575mil,2378.661mil) on Top Layer [Top Solder] Mask Sliver [1.843mil]
Waived by Jeremiah Dados at 3/4/2026 3:12:00 PM

Minimum Solder Mask Sliver Constraint: (1.843mil < 10mil) Between Pad U11-13(3425.787mil,2321.575mil) on Top Layer And Pad U11-7(3376.575mil,2264.488mil) on Top Layer [Top Solder] Mask Sliver [1.843mil]
Waived by Jeremiah Dados at 3/4/2026 3:12:00 PM

Minimum Solder Mask Sliver Constraint: (1.843mil < 10mil) Between Pad U11-13(3425.787mil,2321.575mil) on Top Layer And Pad U11-8(3396.26mil,2264.488mil) on Top Layer [Top Solder] Mask Sliver [1.843mil]
Waived by Jeremiah Dados at 3/4/2026 3:12:00 PM

Minimum Solder Mask Sliver Constraint: (1.843mil < 10mil) Between Pad U11-13(3425.787mil,2321.575mil) on Top Layer And Pad U11-9(3415.945mil,2264.488mil) on Top Layer [Top Solder] Mask Sliver [1.843mil]
Waived by Jeremiah Dados at 3/4/2026 3:12:00 PM

Minimum Solder Mask Sliver Constraint: (1.843mil < 10mil) Between Pad U11-2(3455.315mil,2378.661mil) on Top Layer And Pad U11-3(3435.63mil,2378.661mil) on Top Layer [Top Solder] Mask Sliver [1.843mil]
Waived by Jeremiah Dados at 3/4/2026 3:12:00 PM

Minimum Solder Mask Sliver Constraint: (5.801mil < 10mil) Between Pad U11-2(3455.315mil,2378.661mil) on Top Layer And Via (3465.157mil,2341.26mil) from Top Layer to Bottom Layer [Top Solder] Mask Sliver [5.801mil]
Waived by Jeremiah Dados at 3/4/2026 3:12:00 PM

Minimum Solder Mask Sliver Constraint: (8.685mil < 10mil) Between Pad U1-12(3491.5mil,3016.102mil) on Top Layer And Pad U1-13(3491.5mil,3035.787mil) on Top Layer [Top Solder] Mask Sliver [8.685mil]
Waived by Jeremiah Dados at 3/4/2026 3:12:00 PM

Minimum Solder Mask Sliver Constraint: (1.843mil < 10mil) Between Pad U11-3(3435.63mil,2378.661mil) on Top Layer And Pad U11-4(3415.945mil,2378.661mil) on Top Layer [Top Solder] Mask Sliver [1.843mil]
Waived by Jeremiah Dados at 3/4/2026 3:12:00 PM

Minimum Solder Mask Sliver Constraint: (5.801mil < 10mil) Between Pad U11-3(3435.63mil,2378.661mil) on Top Layer And Via (3425.787mil,2341.26mil) from Top Layer to Bottom Layer [Top Solder] Mask Sliver [5.801mil]
Waived by Jeremiah Dados at 3/4/2026 3:12:00 PM

Minimum Solder Mask Sliver Constraint: (8.685mil < 10mil) Between Pad U1-13(3491.5mil,3035.787mil) on Top Layer And Pad U1-14(3491.5mil,3055.472mil) on Top Layer [Top Solder] Mask Sliver [8.685mil]
Waived by Jeremiah Dados at 3/4/2026 3:12:00 PM

Minimum Solder Mask Sliver Constraint: (1.843mil < 10mil) Between Pad U11-4(3415.945mil,2378.661mil) on Top Layer And Pad U11-5(3396.26mil,2378.661mil) on Top Layer [Top Solder] Mask Sliver [1.843mil]
Waived by Jeremiah Dados at 3/4/2026 3:12:00 PM

Minimum Solder Mask Sliver Constraint: (5.801mil < 10mil) Between Pad U11-4(3415.945mil,2378.661mil) on Top Layer And Via (3425.787mil,2341.26mil) from Top Layer to Bottom Layer [Top Solder] Mask Sliver [5.801mil]
Waived by Jeremiah Dados at 3/4/2026 3:12:00 PM

Minimum Solder Mask Sliver Constraint: (8.685mil < 10mil) Between Pad U1-14(3491.5mil,3055.472mil) on Top Layer And Pad U1-15(3491.5mil,3075.157mil) on Top Layer [Top Solder] Mask Sliver [8.685mil]
Waived by Jeremiah Dados at 3/4/2026 3:12:00 PM

Minimum Solder Mask Sliver Constraint: (1.843mil < 10mil) Between Pad U11-5(3396.26mil,2378.661mil) on Top Layer And Pad U11-6(3376.575mil,2378.661mil) on Top Layer [Top Solder] Mask Sliver [1.843mil]
Waived by Jeremiah Dados at 3/4/2026 3:12:00 PM

Minimum Solder Mask Sliver Constraint: (5.801mil < 10mil) Between Pad U11-5(3396.26mil,2378.661mil) on Top Layer And Via (3386.417mil,2341.26mil) from Top Layer to Bottom Layer [Top Solder] Mask Sliver [5.801mil]
Waived by Jeremiah Dados at 3/4/2026 3:12:00 PM

Minimum Solder Mask Sliver Constraint: (8.685mil < 10mil) Between Pad U1-15(3491.5mil,3075.157mil) on Top Layer And Pad U1-16(3491.5mil,3094.843mil) on Top Layer [Top Solder] Mask Sliver [8.685mil]
Waived by Jeremiah Dados at 3/4/2026 3:12:00 PM

Minimum Solder Mask Sliver Constraint: (5.801mil < 10mil) Between Pad U11-6(3376.575mil,2378.661mil) on Top Layer And Via (3386.417mil,2341.26mil) from Top Layer to Bottom Layer [Top Solder] Mask Sliver [5.801mil]
Waived by Jeremiah Dados at 3/4/2026 3:12:00 PM

Minimum Solder Mask Sliver Constraint: (8.685mil < 10mil) Between Pad U1-16(3491.5mil,3094.843mil) on Top Layer And Pad U1-17(3491.5mil,3114.528mil) on Top Layer [Top Solder] Mask Sliver [8.685mil]
Waived by Jeremiah Dados at 3/4/2026 3:12:00 PM

Minimum Solder Mask Sliver Constraint: (1.843mil < 10mil) Between Pad U11-7(3376.575mil,2264.488mil) on Top Layer And Pad U11-8(3396.26mil,2264.488mil) on Top Layer [Top Solder] Mask Sliver [1.843mil]
Waived by Jeremiah Dados at 3/4/2026 3:12:00 PM

Minimum Solder Mask Sliver Constraint: (5.801mil < 10mil) Between Pad U11-7(3376.575mil,2264.488mil) on Top Layer And Via (3386.417mil,2301.89mil) from Top Layer to Bottom Layer [Top Solder] Mask Sliver [5.801mil]
Waived by Jeremiah Dados at 3/4/2026 3:12:00 PM

Minimum Solder Mask Sliver Constraint: (8.685mil < 10mil) Between Pad U1-17(3491.5mil,3114.528mil) on Top Layer And Pad U1-18(3491.5mil,3134.213mil) on Top Layer [Top Solder] Mask Sliver [8.685mil]
Waived by Jeremiah Dados at 3/4/2026 3:12:00 PM

Minimum Solder Mask Sliver Constraint: (1.843mil < 10mil) Between Pad U11-8(3396.26mil,2264.488mil) on Top Layer And Pad U11-9(3415.945mil,2264.488mil) on Top Layer [Top Solder] Mask Sliver [1.843mil]
Waived by Jeremiah Dados at 3/4/2026 3:12:00 PM

Minimum Solder Mask Sliver Constraint: (5.801mil < 10mil) Between Pad U11-8(3396.26mil,2264.488mil) on Top Layer And Via (3386.417mil,2301.89mil) from Top Layer to Bottom Layer [Top Solder] Mask Sliver [5.801mil]
Waived by Jeremiah Dados at 3/4/2026 3:12:00 PM

Minimum Solder Mask Sliver Constraint: (8.685mil < 10mil) Between Pad U1-18(3491.5mil,3134.213mil) on Top Layer And Pad U1-19(3491.5mil,3153.898mil) on Top Layer [Top Solder] Mask Sliver [8.685mil]
Waived by Jeremiah Dados at 3/4/2026 3:12:00 PM

Minimum Solder Mask Sliver Constraint: (5.801mil < 10mil) Between Pad U11-9(3415.945mil,2264.488mil) on Top Layer And Via (3425.787mil,2301.89mil) from Top Layer to Bottom Layer [Top Solder] Mask Sliver [5.801mil]
Waived by Jeremiah Dados at 3/4/2026 3:12:00 PM

Minimum Solder Mask Sliver Constraint: (8.685mil < 10mil) Between Pad U1-19(3491.5mil,3153.898mil) on Top Layer And Pad U1-20(3491.5mil,3173.583mil) on Top Layer [Top Solder] Mask Sliver [8.685mil]
Waived by Jeremiah Dados at 3/4/2026 3:12:00 PM

Minimum Solder Mask Sliver Constraint: (8.685mil < 10mil) Between Pad U1-2(3318.5mil,3153.898mil) on Top Layer And Pad U1-3(3318.5mil,3134.213mil) on Top Layer [Top Solder] Mask Sliver [8.685mil]
Waived by Jeremiah Dados at 3/4/2026 3:12:00 PM

Minimum Solder Mask Sliver Constraint: (8.685mil < 10mil) Between Pad U1-3(3318.5mil,3134.213mil) on Top Layer And Pad U1-4(3318.5mil,3114.528mil) on Top Layer [Top Solder] Mask Sliver [8.685mil]
Waived by Jeremiah Dados at 3/4/2026 3:12:00 PM

Minimum Solder Mask Sliver Constraint: (8.685mil < 10mil) Between Pad U1-4(3318.5mil,3114.528mil) on Top Layer And Pad U1-5(3318.5mil,3094.843mil) on Top Layer [Top Solder] Mask Sliver [8.685mil]
Waived by Jeremiah Dados at 3/4/2026 3:12:00 PM

Minimum Solder Mask Sliver Constraint: (8.685mil < 10mil) Between Pad U1-5(3318.5mil,3094.843mil) on Top Layer And Pad U1-6(3318.5mil,3075.157mil) on Top Layer [Top Solder] Mask Sliver [8.685mil]
Waived by Jeremiah Dados at 3/4/2026 3:12:00 PM

Minimum Solder Mask Sliver Constraint: (8.685mil < 10mil) Between Pad U1-6(3318.5mil,3075.157mil) on Top Layer And Pad U1-7(3318.5mil,3055.472mil) on Top Layer [Top Solder] Mask Sliver [8.685mil]
Waived by Jeremiah Dados at 3/4/2026 3:12:00 PM

Minimum Solder Mask Sliver Constraint: (8.685mil < 10mil) Between Pad U1-7(3318.5mil,3055.472mil) on Top Layer And Pad U1-8(3318.5mil,3035.787mil) on Top Layer [Top Solder] Mask Sliver [8.685mil]
Waived by Jeremiah Dados at 3/4/2026 3:12:00 PM

Minimum Solder Mask Sliver Constraint: (8.685mil < 10mil) Between Pad U1-8(3318.5mil,3035.787mil) on Top Layer And Pad U1-9(3318.5mil,3016.102mil) on Top Layer [Top Solder] Mask Sliver [8.685mil]
Waived by Jeremiah Dados at 3/4/2026 3:12:00 PM

Minimum Solder Mask Sliver Constraint: (1.843mil < 10mil) Between Pad U2-1(4032.992mil,2329.291mil) on Top Layer And Pad U2-13(4090.079mil,2280.079mil) on Top Layer [Top Solder] Mask Sliver [1.843mil]
Waived by Jeremiah Dados at 11/7/2025 11:43:55 PM

Minimum Solder Mask Sliver Constraint: (1.843mil < 10mil) Between Pad U2-1(4032.992mil,2329.291mil) on Top Layer And Pad U2-2(4032.992mil,2309.606mil) on Top Layer [Top Solder] Mask Sliver [1.843mil]
Waived by Jeremiah Dados at 11/7/2025 11:43:55 PM

Minimum Solder Mask Sliver Constraint: (5.801mil < 10mil) Between Pad U2-1(4032.992mil,2329.291mil) on Top Layer And Via (4070.394mil,2319.449mil) from Top Layer to Bottom Layer [Top Solder] Mask Sliver [5.801mil]
Waived by Jeremiah Dados at 11/7/2025 11:43:55 PM

Minimum Solder Mask Sliver Constraint: (1.843mil < 10mil) Between Pad U2-10(4147.165mil,2289.921mil) on Top Layer And Pad U2-11(4147.165mil,2309.606mil) on Top Layer [Top Solder] Mask Sliver [1.843mil]
Waived by Jeremiah Dados at 3/1/2026 3:46:15 PM

Minimum Solder Mask Sliver Constraint: (1.843mil < 10mil) Between Pad U2-10(4147.165mil,2289.921mil) on Top Layer And Pad U2-13(4090.079mil,2280.079mil) on Top Layer [Top Solder] Mask Sliver [1.843mil]
Waived by Jeremiah Dados at 11/7/2025 11:43:55 PM

Minimum Solder Mask Sliver Constraint: (1.843mil < 10mil) Between Pad U2-10(4147.165mil,2289.921mil) on Top Layer And Pad U2-9(4147.165mil,2270.236mil) on Top Layer [Top Solder] Mask Sliver [1.843mil]
Waived by Jeremiah Dados at 11/7/2025 11:43:55 PM

Minimum Solder Mask Sliver Constraint: (5.801mil < 10mil) Between Pad U2-10(4147.165mil,2289.921mil) on Top Layer And Via (4109.764mil,2280.079mil) from Top Layer to Bottom Layer [Top Solder] Mask Sliver [5.801mil]
Waived by Jeremiah Dados at 11/7/2025 11:43:55 PM

Minimum Solder Mask Sliver Constraint: (1.843mil < 10mil) Between Pad U2-11(4147.165mil,2309.606mil) on Top Layer And Pad U2-12(4147.165mil,2329.291mil) on Top Layer [Top Solder] Mask Sliver [1.843mil]
Waived by Jeremiah Dados at 3/1/2026 3:46:15 PM

Minimum Solder Mask Sliver Constraint: (1.843mil < 10mil) Between Pad U2-11(4147.165mil,2309.606mil) on Top Layer And Pad U2-13(4090.079mil,2280.079mil) on Top Layer [Top Solder] Mask Sliver [1.843mil]
Waived by Jeremiah Dados at 3/1/2026 3:46:15 PM

Minimum Solder Mask Sliver Constraint: (5.801mil < 10mil) Between Pad U2-11(4147.165mil,2309.606mil) on Top Layer And Via (4109.764mil,2319.449mil) from Top Layer to Bottom Layer [Top Solder] Mask Sliver [5.801mil]
Waived by Jeremiah Dados at 3/1/2026 3:46:15 PM

Minimum Solder Mask Sliver Constraint: (1.843mil < 10mil) Between Pad U2-12(4147.165mil,2329.291mil) on Top Layer And Pad U2-13(4090.079mil,2280.079mil) on Top Layer [Top Solder] Mask Sliver [1.843mil]
Waived by Jeremiah Dados at 3/1/2026 3:46:15 PM

Minimum Solder Mask Sliver Constraint: (5.801mil < 10mil) Between Pad U2-12(4147.165mil,2329.291mil) on Top Layer And Via (4109.764mil,2319.449mil) from Top Layer to Bottom Layer [Top Solder] Mask Sliver [5.801mil]
Waived by Jeremiah Dados at 3/1/2026 3:46:15 PM

Minimum Solder Mask Sliver Constraint: (1.843mil < 10mil) Between Pad U2-13(4090.079mil,2280.079mil) on Top Layer And Pad U2-2(4032.992mil,2309.606mil) on Top Layer [Top Solder] Mask Sliver [1.843mil]
Waived by Jeremiah Dados at 11/7/2025 11:43:55 PM

Minimum Solder Mask Sliver Constraint: (1.843mil < 10mil) Between Pad U2-13(4090.079mil,2280.079mil) on Top Layer And Pad U2-3(4032.992mil,2289.921mil) on Top Layer [Top Solder] Mask Sliver [1.843mil]
Waived by Jeremiah Dados at 11/7/2025 11:43:55 PM

Minimum Solder Mask Sliver Constraint: (1.843mil < 10mil) Between Pad U2-13(4090.079mil,2280.079mil) on Top Layer And Pad U2-4(4032.992mil,2270.236mil) on Top Layer [Top Solder] Mask Sliver [1.843mil]
Waived by Jeremiah Dados at 11/7/2025 11:43:55 PM

Minimum Solder Mask Sliver Constraint: (1.843mil < 10mil) Between Pad U2-13(4090.079mil,2280.079mil) on Top Layer And Pad U2-5(4032.992mil,2250.551mil) on Top Layer [Top Solder] Mask Sliver [1.843mil]
Waived by Jeremiah Dados at 11/7/2025 11:43:55 PM

Minimum Solder Mask Sliver Constraint: (1.843mil < 10mil) Between Pad U2-13(4090.079mil,2280.079mil) on Top Layer And Pad U2-6(4032.992mil,2230.866mil) on Top Layer [Top Solder] Mask Sliver [1.843mil]
Waived by Jeremiah Dados at 3/1/2026 3:46:15 PM

Minimum Solder Mask Sliver Constraint: (1.843mil < 10mil) Between Pad U2-13(4090.079mil,2280.079mil) on Top Layer And Pad U2-7(4147.165mil,2230.866mil) on Top Layer [Top Solder] Mask Sliver [1.843mil]
Waived by Jeremiah Dados at 3/1/2026 3:46:15 PM

Minimum Solder Mask Sliver Constraint: (1.843mil < 10mil) Between Pad U2-13(4090.079mil,2280.079mil) on Top Layer And Pad U2-8(4147.165mil,2250.551mil) on Top Layer [Top Solder] Mask Sliver [1.843mil]
Waived by Jeremiah Dados at 11/7/2025 11:43:55 PM

Minimum Solder Mask Sliver Constraint: (1.843mil < 10mil) Between Pad U2-13(4090.079mil,2280.079mil) on Top Layer And Pad U2-9(4147.165mil,2270.236mil) on Top Layer [Top Solder] Mask Sliver [1.843mil]
Waived by Jeremiah Dados at 11/7/2025 11:43:55 PM

Minimum Solder Mask Sliver Constraint: (1.843mil < 10mil) Between Pad U2-2(4032.992mil,2309.606mil) on Top Layer And Pad U2-3(4032.992mil,2289.921mil) on Top Layer [Top Solder] Mask Sliver [1.843mil]
Waived by Jeremiah Dados at 11/7/2025 11:43:55 PM

Minimum Solder Mask Sliver Constraint: (5.801mil < 10mil) Between Pad U2-2(4032.992mil,2309.606mil) on Top Layer And Via (4070.394mil,2319.449mil) from Top Layer to Bottom Layer [Top Solder] Mask Sliver [5.801mil]
Waived by Jeremiah Dados at 11/7/2025 11:43:55 PM

Minimum Solder Mask Sliver Constraint: (1.843mil < 10mil) Between Pad U2-3(4032.992mil,2289.921mil) on Top Layer And Pad U2-4(4032.992mil,2270.236mil) on Top Layer [Top Solder] Mask Sliver [1.843mil]
Waived by Jeremiah Dados at 11/7/2025 11:43:55 PM

Minimum Solder Mask Sliver Constraint: (5.801mil < 10mil) Between Pad U2-3(4032.992mil,2289.921mil) on Top Layer And Via (4070.394mil,2280.079mil) from Top Layer to Bottom Layer [Top Solder] Mask Sliver [5.801mil]
Waived by Jeremiah Dados at 11/7/2025 11:43:55 PM

Minimum Solder Mask Sliver Constraint: (1.843mil < 10mil) Between Pad U2-4(4032.992mil,2270.236mil) on Top Layer And Pad U2-5(4032.992mil,2250.551mil) on Top Layer [Top Solder] Mask Sliver [1.843mil]
Waived by Jeremiah Dados at 11/7/2025 11:43:55 PM

Minimum Solder Mask Sliver Constraint: (5.801mil < 10mil) Between Pad U2-4(4032.992mil,2270.236mil) on Top Layer And Via (4070.394mil,2280.079mil) from Top Layer to Bottom Layer [Top Solder] Mask Sliver [5.801mil]
Waived by Jeremiah Dados at 11/7/2025 11:43:55 PM

Minimum Solder Mask Sliver Constraint: (1.843mil < 10mil) Between Pad U2-5(4032.992mil,2250.551mil) on Top Layer And Pad U2-6(4032.992mil,2230.866mil) on Top Layer [Top Solder] Mask Sliver [1.843mil]
Waived by Jeremiah Dados at 3/1/2026 3:46:15 PM

Minimum Solder Mask Sliver Constraint: (5.801mil < 10mil) Between Pad U2-5(4032.992mil,2250.551mil) on Top Layer And Via (4070.394mil,2240.709mil) from Top Layer to Bottom Layer [Top Solder] Mask Sliver [5.801mil]
Waived by Jeremiah Dados at 11/7/2025 11:43:55 PM

Minimum Solder Mask Sliver Constraint: (5.801mil < 10mil) Between Pad U2-6(4032.992mil,2230.866mil) on Top Layer And Via (4070.394mil,2240.709mil) from Top Layer to Bottom Layer [Top Solder] Mask Sliver [5.801mil]
Waived by Jeremiah Dados at 3/1/2026 3:46:15 PM

Minimum Solder Mask Sliver Constraint: (1.843mil < 10mil) Between Pad U2-7(4147.165mil,2230.866mil) on Top Layer And Pad U2-8(4147.165mil,2250.551mil) on Top Layer [Top Solder] Mask Sliver [1.843mil]
Waived by Jeremiah Dados at 3/1/2026 3:46:15 PM

Minimum Solder Mask Sliver Constraint: (5.801mil < 10mil) Between Pad U2-7(4147.165mil,2230.866mil) on Top Layer And Via (4109.764mil,2240.709mil) from Top Layer to Bottom Layer [Top Solder] Mask Sliver [5.801mil]
Waived by Jeremiah Dados at 3/1/2026 3:46:15 PM

Minimum Solder Mask Sliver Constraint: (1.843mil < 10mil) Between Pad U2-8(4147.165mil,2250.551mil) on Top Layer And Pad U2-9(4147.165mil,2270.236mil) on Top Layer [Top Solder] Mask Sliver [1.843mil]
Waived by Jeremiah Dados at 11/7/2025 11:43:55 PM

Minimum Solder Mask Sliver Constraint: (5.801mil < 10mil) Between Pad U2-8(4147.165mil,2250.551mil) on Top Layer And Via (4109.764mil,2240.709mil) from Top Layer to Bottom Layer [Top Solder] Mask Sliver [5.801mil]
Waived by Jeremiah Dados at 11/7/2025 11:43:55 PM

Minimum Solder Mask Sliver Constraint: (5.801mil < 10mil) Between Pad U2-9(4147.165mil,2270.236mil) on Top Layer And Via (4109.764mil,2280.079mil) from Top Layer to Bottom Layer [Top Solder] Mask Sliver [5.801mil]
Waived by Jeremiah Dados at 11/7/2025 11:43:55 PM

Minimum Solder Mask Sliver Constraint: (8.76mil < 10mil) Between Pad U5-1(4326.413mil,2719.168mil) on Top Layer And Pad U5-7(4289.012mil,2667.987mil) on Top Layer [Top Solder] Mask Sliver [8.76mil]
Waived by Jeremiah Dados at 3/1/2026 3:46:15 PM

Minimum Solder Mask Sliver Constraint: (9.603mil < 10mil) Between Pad U5-2(4289.012mil,2720.012mil) on Top Layer And Pad U5-7(4289.012mil,2667.987mil) on Top Layer [Top Solder] Mask Sliver [9.604mil]
Waived by Jeremiah Dados at 3/1/2026 3:46:15 PM

Minimum Solder Mask Sliver Constraint: (9.603mil < 10mil) Between Pad U5-3(4251.61mil,2720.012mil) on Top Layer And Pad U5-7(4289.012mil,2667.987mil) on Top Layer [Top Solder] Mask Sliver [9.604mil]
Waived by Jeremiah Dados at 3/1/2026 3:46:15 PM

Minimum Solder Mask Sliver Constraint: (8.76mil < 10mil) Between Pad U5-4(4251.61mil,2616.806mil) on Top Layer And Pad U5-7(4289.012mil,2667.987mil) on Top Layer [Top Solder] Mask Sliver [8.76mil]
Waived by Jeremiah Dados at 3/1/2026 3:46:15 PM

Minimum Solder Mask Sliver Constraint: (9.604mil < 10mil) Between Pad U5-5(4289.012mil,2615.962mil) on Top Layer And Pad U5-7(4289.012mil,2667.987mil) on Top Layer [Top Solder] Mask Sliver [9.604mil]
Waived by Jeremiah Dados at 3/1/2026 3:46:15 PM

Minimum Solder Mask Sliver Constraint: (9.604mil < 10mil) Between Pad U5-6(4326.413mil,2615.962mil) on Top Layer And Pad U5-7(4289.012mil,2667.987mil) on Top Layer [Top Solder] Mask Sliver [9.604mil]
Waived by Jeremiah Dados at 3/1/2026 3:46:15 PM

Minimum Solder Mask Sliver Constraint: (0.661mil < 10mil) Between Pad U6-1(5066.93mil,2192.753mil) on Top Layer And Pad U6-2(5066.93mil,2212.438mil) on Top Layer [Top Solder] Mask Sliver [0.661mil]
Waived by Jeremiah Dados at 3/5/2026 5:07:27 PM

Minimum Solder Mask Sliver Constraint: (0.661mil < 10mil) Between Pad U6-10(5066.93mil,2369.919mil) on Top Layer And Pad U6-11(5066.93mil,2389.604mil) on Top Layer [Top Solder] Mask Sliver [0.661mil]
Waived by Jeremiah Dados at 3/5/2026 5:07:27 PM

Minimum Solder Mask Sliver Constraint: (0.662mil < 10mil) Between Pad U6-10(5066.93mil,2369.919mil) on Top Layer And Pad U6-9(5066.93mil,2350.234mil) on Top Layer [Top Solder] Mask Sliver [0.662mil]
Waived by Jeremiah Dados at 3/5/2026 5:07:27 PM

Minimum Solder Mask Sliver Constraint: (0.661mil < 10mil) Between Pad U6-11(5066.93mil,2389.604mil) on Top Layer And Pad U6-12(5066.93mil,2409.289mil) on Top Layer [Top Solder] Mask Sliver [0.661mil]
Waived by Jeremiah Dados at 3/5/2026 5:07:27 PM

Minimum Solder Mask Sliver Constraint: (0.662mil < 10mil) Between Pad U6-12(5066.93mil,2409.289mil) on Top Layer And Pad U6-13(5066.93mil,2428.974mil) on Top Layer [Top Solder] Mask Sliver [0.662mil]
Waived by Jeremiah Dados at 3/5/2026 5:07:27 PM

Minimum Solder Mask Sliver Constraint: (0.661mil < 10mil) Between Pad U6-13(5066.93mil,2428.974mil) on Top Layer And Pad U6-14(5066.93mil,2448.659mil) on Top Layer [Top Solder] Mask Sliver [0.661mil]
Waived by Jeremiah Dados at 3/5/2026 5:07:27 PM

Minimum Solder Mask Sliver Constraint: (0.662mil < 10mil) Between Pad U6-14(5066.93mil,2448.659mil) on Top Layer And Pad U6-15(5066.93mil,2468.344mil) on Top Layer [Top Solder] Mask Sliver [0.662mil]
Waived by Jeremiah Dados at 3/5/2026 5:07:27 PM

Minimum Solder Mask Sliver Constraint: (0.661mil < 10mil) Between Pad U6-15(5066.93mil,2468.344mil) on Top Layer And Pad U6-16(5066.93mil,2488.029mil) on Top Layer [Top Solder] Mask Sliver [0.661mil]
Waived by Jeremiah Dados at 3/5/2026 5:07:27 PM

Minimum Solder Mask Sliver Constraint: (0.661mil < 10mil) Between Pad U6-17(4990.946mil,2564.013mil) on Top Layer And Pad U6-18(4971.261mil,2564.013mil) on Top Layer [Top Solder] Mask Sliver [0.661mil]
Waived by Jeremiah Dados at 3/5/2026 5:07:27 PM

Minimum Solder Mask Sliver Constraint: (0.662mil < 10mil) Between Pad U6-18(4971.261mil,2564.013mil) on Top Layer And Pad U6-19(4951.576mil,2564.013mil) on Top Layer [Top Solder] Mask Sliver [0.662mil]
Waived by Jeremiah Dados at 3/5/2026 5:07:27 PM

Minimum Solder Mask Sliver Constraint: (0.661mil < 10mil) Between Pad U6-19(4951.576mil,2564.013mil) on Top Layer And Pad U6-20(4931.891mil,2564.013mil) on Top Layer [Top Solder] Mask Sliver [0.661mil]
Waived by Jeremiah Dados at 3/5/2026 5:07:27 PM

Minimum Solder Mask Sliver Constraint: (0.662mil < 10mil) Between Pad U6-2(5066.93mil,2212.438mil) on Top Layer And Pad U6-3(5066.93mil,2232.123mil) on Top Layer [Top Solder] Mask Sliver [0.662mil]
Waived by Jeremiah Dados at 3/5/2026 5:07:27 PM

Minimum Solder Mask Sliver Constraint: (0.662mil < 10mil) Between Pad U6-20(4931.891mil,2564.013mil) on Top Layer And Pad U6-21(4912.206mil,2564.013mil) on Top Layer [Top Solder] Mask Sliver [0.662mil]
Waived by Jeremiah Dados at 3/5/2026 5:07:27 PM

Minimum Solder Mask Sliver Constraint: (0.661mil < 10mil) Between Pad U6-21(4912.206mil,2564.013mil) on Top Layer And Pad U6-22(4892.521mil,2564.013mil) on Top Layer [Top Solder] Mask Sliver [0.661mil]
Waived by Jeremiah Dados at 3/5/2026 5:07:27 PM

Minimum Solder Mask Sliver Constraint: (0.661mil < 10mil) Between Pad U6-22(4892.521mil,2564.013mil) on Top Layer And Pad U6-23(4872.836mil,2564.013mil) on Top Layer [Top Solder] Mask Sliver [0.661mil]
Waived by Jeremiah Dados at 3/5/2026 5:07:27 PM

Minimum Solder Mask Sliver Constraint: (0.662mil < 10mil) Between Pad U6-23(4872.836mil,2564.013mil) on Top Layer And Pad U6-24(4853.151mil,2564.013mil) on Top Layer [Top Solder] Mask Sliver [0.662mil]
Waived by Jeremiah Dados at 3/5/2026 5:07:27 PM

Minimum Solder Mask Sliver Constraint: (0.661mil < 10mil) Between Pad U6-24(4853.151mil,2564.013mil) on Top Layer And Pad U6-25(4833.466mil,2564.013mil) on Top Layer [Top Solder] Mask Sliver [0.661mil]
Waived by Jeremiah Dados at 3/5/2026 5:07:27 PM

Minimum Solder Mask Sliver Constraint: (0.662mil < 10mil) Between Pad U6-25(4833.466mil,2564.013mil) on Top Layer And Pad U6-26(4813.78mil,2564.013mil) on Top Layer [Top Solder] Mask Sliver [0.662mil]
Waived by Jeremiah Dados at 3/5/2026 5:07:27 PM

Minimum Solder Mask Sliver Constraint: (0.661mil < 10mil) Between Pad U6-26(4813.78mil,2564.013mil) on Top Layer And Pad U6-27(4794.096mil,2564.013mil) on Top Layer [Top Solder] Mask Sliver [0.661mil]
Waived by Jeremiah Dados at 3/5/2026 5:07:27 PM

Minimum Solder Mask Sliver Constraint: (0.661mil < 10mil) Between Pad U6-27(4794.096mil,2564.013mil) on Top Layer And Pad U6-28(4774.41mil,2564.013mil) on Top Layer [Top Solder] Mask Sliver [0.661mil]
Waived by Jeremiah Dados at 3/5/2026 5:07:27 PM

Minimum Solder Mask Sliver Constraint: (0.662mil < 10mil) Between Pad U6-28(4774.41mil,2564.013mil) on Top Layer And Pad U6-29(4754.725mil,2564.013mil) on Top Layer [Top Solder] Mask Sliver [0.662mil]
Waived by Jeremiah Dados at 3/5/2026 5:07:27 PM

Minimum Solder Mask Sliver Constraint: (0.661mil < 10mil) Between Pad U6-29(4754.725mil,2564.013mil) on Top Layer And Pad U6-30(4735.04mil,2564.013mil) on Top Layer [Top Solder] Mask Sliver [0.661mil]
Waived by Jeremiah Dados at 3/5/2026 5:07:27 PM

Minimum Solder Mask Sliver Constraint: (0.661mil < 10mil) Between Pad U6-3(5066.93mil,2232.123mil) on Top Layer And Pad U6-4(5066.93mil,2251.808mil) on Top Layer [Top Solder] Mask Sliver [0.661mil]
Waived by Jeremiah Dados at 3/5/2026 5:07:27 PM

Minimum Solder Mask Sliver Constraint: (0.662mil < 10mil) Between Pad U6-30(4735.04mil,2564.013mil) on Top Layer And Pad U6-31(4715.355mil,2564.013mil) on Top Layer [Top Solder] Mask Sliver [0.662mil]
Waived by Jeremiah Dados at 3/5/2026 5:07:27 PM

Minimum Solder Mask Sliver Constraint: (0.661mil < 10mil) Between Pad U6-31(4715.355mil,2564.013mil) on Top Layer And Pad U6-32(4695.67mil,2564.013mil) on Top Layer [Top Solder] Mask Sliver [0.661mil]
Waived by Jeremiah Dados at 3/5/2026 5:07:27 PM

Minimum Solder Mask Sliver Constraint: (0.661mil < 10mil) Between Pad U6-33(4619.686mil,2488.029mil) on Top Layer And Pad U6-34(4619.686mil,2468.344mil) on Top Layer [Top Solder] Mask Sliver [0.661mil]
Waived by Jeremiah Dados at 3/5/2026 5:07:27 PM

Minimum Solder Mask Sliver Constraint: (0.662mil < 10mil) Between Pad U6-34(4619.686mil,2468.344mil) on Top Layer And Pad U6-35(4619.686mil,2448.659mil) on Top Layer [Top Solder] Mask Sliver [0.662mil]
Waived by Jeremiah Dados at 3/5/2026 5:07:27 PM

Minimum Solder Mask Sliver Constraint: (0.661mil < 10mil) Between Pad U6-35(4619.686mil,2448.659mil) on Top Layer And Pad U6-36(4619.686mil,2428.974mil) on Top Layer [Top Solder] Mask Sliver [0.661mil]
Waived by Jeremiah Dados at 3/5/2026 5:07:27 PM

Minimum Solder Mask Sliver Constraint: (0.662mil < 10mil) Between Pad U6-36(4619.686mil,2428.974mil) on Top Layer And Pad U6-37(4619.686mil,2409.289mil) on Top Layer [Top Solder] Mask Sliver [0.662mil]
Waived by Jeremiah Dados at 3/5/2026 5:07:27 PM

Minimum Solder Mask Sliver Constraint: (0.661mil < 10mil) Between Pad U6-37(4619.686mil,2409.289mil) on Top Layer And Pad U6-38(4619.686mil,2389.604mil) on Top Layer [Top Solder] Mask Sliver [0.661mil]
Waived by Jeremiah Dados at 3/5/2026 5:07:27 PM

Minimum Solder Mask Sliver Constraint: (0.661mil < 10mil) Between Pad U6-38(4619.686mil,2389.604mil) on Top Layer And Pad U6-39(4619.686mil,2369.919mil) on Top Layer [Top Solder] Mask Sliver [0.661mil]
Waived by Jeremiah Dados at 3/5/2026 5:07:27 PM

Minimum Solder Mask Sliver Constraint: (0.662mil < 10mil) Between Pad U6-39(4619.686mil,2369.919mil) on Top Layer And Pad U6-40(4619.686mil,2350.234mil) on Top Layer [Top Solder] Mask Sliver [0.662mil]
Waived by Jeremiah Dados at 3/5/2026 5:07:27 PM

Minimum Solder Mask Sliver Constraint: (0.662mil < 10mil) Between Pad U6-4(5066.93mil,2251.808mil) on Top Layer And Pad U6-5(5066.93mil,2271.494mil) on Top Layer [Top Solder] Mask Sliver [0.662mil]
Waived by Jeremiah Dados at 3/5/2026 5:07:27 PM

Minimum Solder Mask Sliver Constraint: (0.661mil < 10mil) Between Pad U6-40(4619.686mil,2350.234mil) on Top Layer And Pad U6-41(4619.686mil,2330.549mil) on Top Layer [Top Solder] Mask Sliver [0.661mil]
Waived by Jeremiah Dados at 3/5/2026 5:07:27 PM

Minimum Solder Mask Sliver Constraint: (0.662mil < 10mil) Between Pad U6-41(4619.686mil,2330.549mil) on Top Layer And Pad U6-42(4619.686mil,2310.863mil) on Top Layer [Top Solder] Mask Sliver [0.662mil]
Waived by Jeremiah Dados at 3/5/2026 5:07:27 PM

Minimum Solder Mask Sliver Constraint: (0.661mil < 10mil) Between Pad U6-42(4619.686mil,2310.863mil) on Top Layer And Pad U6-43(4619.686mil,2291.178mil) on Top Layer [Top Solder] Mask Sliver [0.661mil]
Waived by Jeremiah Dados at 3/5/2026 5:07:27 PM

Minimum Solder Mask Sliver Constraint: (0.661mil < 10mil) Between Pad U6-43(4619.686mil,2291.178mil) on Top Layer And Pad U6-44(4619.686mil,2271.494mil) on Top Layer [Top Solder] Mask Sliver [0.661mil]
Waived by Jeremiah Dados at 3/5/2026 5:07:27 PM

Minimum Solder Mask Sliver Constraint: (0.662mil < 10mil) Between Pad U6-44(4619.686mil,2271.494mil) on Top Layer And Pad U6-45(4619.686mil,2251.808mil) on Top Layer [Top Solder] Mask Sliver [0.662mil]
Waived by Jeremiah Dados at 3/5/2026 5:07:27 PM

Minimum Solder Mask Sliver Constraint: (0.661mil < 10mil) Between Pad U6-45(4619.686mil,2251.808mil) on Top Layer And Pad U6-46(4619.686mil,2232.123mil) on Top Layer [Top Solder] Mask Sliver [0.661mil]
Waived by Jeremiah Dados at 3/5/2026 5:07:27 PM

Minimum Solder Mask Sliver Constraint: (0.662mil < 10mil) Between Pad U6-46(4619.686mil,2232.123mil) on Top Layer And Pad U6-47(4619.686mil,2212.438mil) on Top Layer [Top Solder] Mask Sliver [0.662mil]
Waived by Jeremiah Dados at 3/5/2026 5:07:27 PM

Minimum Solder Mask Sliver Constraint: (0.661mil < 10mil) Between Pad U6-47(4619.686mil,2212.438mil) on Top Layer And Pad U6-48(4619.686mil,2192.753mil) on Top Layer [Top Solder] Mask Sliver [0.661mil]
Waived by Jeremiah Dados at 3/5/2026 5:07:27 PM

Minimum Solder Mask Sliver Constraint: (0.661mil < 10mil) Between Pad U6-49(4695.67mil,2116.769mil) on Top Layer And Pad U6-50(4715.355mil,2116.769mil) on Top Layer [Top Solder] Mask Sliver [0.661mil]
Waived by Jeremiah Dados at 3/5/2026 5:07:27 PM

Minimum Solder Mask Sliver Constraint: (0.661mil < 10mil) Between Pad U6-5(5066.93mil,2271.494mil) on Top Layer And Pad U6-6(5066.93mil,2291.178mil) on Top Layer [Top Solder] Mask Sliver [0.661mil]
Waived by Jeremiah Dados at 3/5/2026 5:07:27 PM

Minimum Solder Mask Sliver Constraint: (0.662mil < 10mil) Between Pad U6-50(4715.355mil,2116.769mil) on Top Layer And Pad U6-51(4735.04mil,2116.769mil) on Top Layer [Top Solder] Mask Sliver [0.662mil]
Waived by Jeremiah Dados at 3/5/2026 5:07:27 PM

Minimum Solder Mask Sliver Constraint: (0.661mil < 10mil) Between Pad U6-51(4735.04mil,2116.769mil) on Top Layer And Pad U6-52(4754.725mil,2116.769mil) on Top Layer [Top Solder] Mask Sliver [0.661mil]
Waived by Jeremiah Dados at 3/5/2026 5:07:27 PM

Minimum Solder Mask Sliver Constraint: (0.662mil < 10mil) Between Pad U6-52(4754.725mil,2116.769mil) on Top Layer And Pad U6-53(4774.41mil,2116.769mil) on Top Layer [Top Solder] Mask Sliver [0.662mil]
Waived by Jeremiah Dados at 3/5/2026 5:07:27 PM

Minimum Solder Mask Sliver Constraint: (0.661mil < 10mil) Between Pad U6-53(4774.41mil,2116.769mil) on Top Layer And Pad U6-54(4794.096mil,2116.769mil) on Top Layer [Top Solder] Mask Sliver [0.661mil]
Waived by Jeremiah Dados at 3/5/2026 5:07:27 PM

Minimum Solder Mask Sliver Constraint: (0.661mil < 10mil) Between Pad U6-54(4794.096mil,2116.769mil) on Top Layer And Pad U6-55(4813.78mil,2116.769mil) on Top Layer [Top Solder] Mask Sliver [0.661mil]
Waived by Jeremiah Dados at 3/5/2026 5:07:27 PM

Minimum Solder Mask Sliver Constraint: (0.662mil < 10mil) Between Pad U6-55(4813.78mil,2116.769mil) on Top Layer And Pad U6-56(4833.466mil,2116.769mil) on Top Layer [Top Solder] Mask Sliver [0.662mil]
Waived by Jeremiah Dados at 3/5/2026 5:07:27 PM

Minimum Solder Mask Sliver Constraint: (0.661mil < 10mil) Between Pad U6-56(4833.466mil,2116.769mil) on Top Layer And Pad U6-57(4853.151mil,2116.769mil) on Top Layer [Top Solder] Mask Sliver [0.661mil]
Waived by Jeremiah Dados at 3/5/2026 5:07:27 PM

Minimum Solder Mask Sliver Constraint: (0.662mil < 10mil) Between Pad U6-57(4853.151mil,2116.769mil) on Top Layer And Pad U6-58(4872.836mil,2116.769mil) on Top Layer [Top Solder] Mask Sliver [0.662mil]
Waived by Jeremiah Dados at 3/5/2026 5:07:27 PM

Minimum Solder Mask Sliver Constraint: (0.661mil < 10mil) Between Pad U6-58(4872.836mil,2116.769mil) on Top Layer And Pad U6-59(4892.521mil,2116.769mil) on Top Layer [Top Solder] Mask Sliver [0.661mil]
Waived by Jeremiah Dados at 3/5/2026 5:07:27 PM

Minimum Solder Mask Sliver Constraint: (0.661mil < 10mil) Between Pad U6-59(4892.521mil,2116.769mil) on Top Layer And Pad U6-60(4912.206mil,2116.769mil) on Top Layer [Top Solder] Mask Sliver [0.661mil]
Waived by Jeremiah Dados at 3/5/2026 5:07:27 PM

Minimum Solder Mask Sliver Constraint: (0.661mil < 10mil) Between Pad U6-6(5066.93mil,2291.178mil) on Top Layer And Pad U6-7(5066.93mil,2310.863mil) on Top Layer [Top Solder] Mask Sliver [0.661mil]
Waived by Jeremiah Dados at 3/5/2026 5:07:27 PM

Minimum Solder Mask Sliver Constraint: (0.662mil < 10mil) Between Pad U6-60(4912.206mil,2116.769mil) on Top Layer And Pad U6-61(4931.891mil,2116.769mil) on Top Layer [Top Solder] Mask Sliver [0.662mil]
Waived by Jeremiah Dados at 3/5/2026 5:07:27 PM

Minimum Solder Mask Sliver Constraint: (0.661mil < 10mil) Between Pad U6-61(4931.891mil,2116.769mil) on Top Layer And Pad U6-62(4951.576mil,2116.769mil) on Top Layer [Top Solder] Mask Sliver [0.661mil]
Waived by Jeremiah Dados at 3/5/2026 5:07:27 PM

Minimum Solder Mask Sliver Constraint: (0.662mil < 10mil) Between Pad U6-62(4951.576mil,2116.769mil) on Top Layer And Pad U6-63(4971.261mil,2116.769mil) on Top Layer [Top Solder] Mask Sliver [0.662mil]
Waived by Jeremiah Dados at 3/5/2026 5:07:27 PM

Minimum Solder Mask Sliver Constraint: (0.661mil < 10mil) Between Pad U6-63(4971.261mil,2116.769mil) on Top Layer And Pad U6-64(4990.946mil,2116.769mil) on Top Layer [Top Solder] Mask Sliver [0.661mil]
Waived by Jeremiah Dados at 3/5/2026 5:07:27 PM

Minimum Solder Mask Sliver Constraint: (0.662mil < 10mil) Between Pad U6-7(5066.93mil,2310.863mil) on Top Layer And Pad U6-8(5066.93mil,2330.549mil) on Top Layer [Top Solder] Mask Sliver [0.662mil]
Waived by Jeremiah Dados at 3/5/2026 5:07:27 PM

Minimum Solder Mask Sliver Constraint: (0.661mil < 10mil) Between Pad U6-8(5066.93mil,2330.549mil) on Top Layer And Pad U6-9(5066.93mil,2350.234mil) on Top Layer [Top Solder] Mask Sliver [0.661mil]
Waived by Jeremiah Dados at 3/5/2026 5:07:27 PM

Minimum Solder Mask Sliver Constraint: (1.843mil < 10mil) Between Pad U7-1(4375.63mil,3120.591mil) on Top Layer And Pad U7-2(4375.63mil,3095mil) on Top Layer [Top Solder] Mask Sliver [1.843mil]
Waived by Jeremiah Dados at 11/7/2025 11:43:55 PM

Minimum Solder Mask Sliver Constraint: (1.843mil < 10mil) Between Pad U7-2(4375.63mil,3095mil) on Top Layer And Pad U7-3(4375.63mil,3069.409mil) on Top Layer [Top Solder] Mask Sliver [1.843mil]
Waived by Jeremiah Dados at 11/7/2025 11:43:55 PM

Minimum Solder Mask Sliver Constraint: (1.843mil < 10mil) Between Pad U7-4(4454.37mil,3069.409mil) on Top Layer And Pad U7-5(4454.37mil,3095mil) on Top Layer [Top Solder] Mask Sliver [1.843mil]
Waived by Jeremiah Dados at 11/7/2025 11:43:55 PM

Minimum Solder Mask Sliver Constraint: (1.843mil < 10mil) Between Pad U7-5(4454.37mil,3095mil) on Top Layer And Pad U7-6(4454.37mil,3120.591mil) on Top Layer [Top Solder] Mask Sliver [1.843mil]
Waived by Jeremiah Dados at 11/7/2025 11:43:55 PM

Minimum Solder Mask Sliver Constraint: (9.009mil < 10mil) Between Pad U9-1(4807.913mil,3085.079mil) on Top Layer And Pad U9-12(4844.921mil,3122.087mil) on Top Layer [Top Solder] Mask Sliver [9.009mil]
Waived by Jeremiah Dados at 11/7/2025 11:43:55 PM

Minimum Solder Mask Sliver Constraint: (3.811mil < 10mil) Between Pad U9-1(4807.913mil,3085.079mil) on Top Layer And Pad U9-13(4865mil,3065mil) on Top Layer [Top Solder] Mask Sliver [3.811mil]
Waived by Jeremiah Dados at 11/7/2025 11:43:55 PM

Minimum Solder Mask Sliver Constraint: (0.268mil < 10mil) Between Pad U9-1(4807.913mil,3085.079mil) on Top Layer And Pad U9-2(4807.913mil,3065mil) on Top Layer [Top Solder] Mask Sliver [0.268mil]
Waived by Jeremiah Dados at 11/7/2025 11:43:55 PM

Minimum Solder Mask Sliver Constraint: (0.268mil < 10mil) Between Pad U9-10(4885.079mil,3122.087mil) on Top Layer And Pad U9-11(4865mil,3122.087mil) on Top Layer [Top Solder] Mask Sliver [0.268mil]
Waived by Jeremiah Dados at 11/7/2025 11:43:55 PM

Minimum Solder Mask Sliver Constraint: (3.811mil < 10mil) Between Pad U9-10(4885.079mil,3122.087mil) on Top Layer And Pad U9-13(4865mil,3065mil) on Top Layer [Top Solder] Mask Sliver [3.811mil]
Waived by Jeremiah Dados at 11/7/2025 11:43:55 PM

Minimum Solder Mask Sliver Constraint: (9.009mil < 10mil) Between Pad U9-10(4885.079mil,3122.087mil) on Top Layer And Pad U9-9(4922.087mil,3085.079mil) on Top Layer [Top Solder] Mask Sliver [9.009mil]
Waived by Jeremiah Dados at 11/7/2025 11:43:55 PM

Minimum Solder Mask Sliver Constraint: (0.268mil < 10mil) Between Pad U9-11(4865mil,3122.087mil) on Top Layer And Pad U9-12(4844.921mil,3122.087mil) on Top Layer [Top Solder] Mask Sliver [0.268mil]
Waived by Jeremiah Dados at 11/7/2025 11:43:55 PM

Minimum Solder Mask Sliver Constraint: (3.811mil < 10mil) Between Pad U9-11(4865mil,3122.087mil) on Top Layer And Pad U9-13(4865mil,3065mil) on Top Layer [Top Solder] Mask Sliver [3.811mil]
Waived by Jeremiah Dados at 11/7/2025 11:43:55 PM

Minimum Solder Mask Sliver Constraint: (3.811mil < 10mil) Between Pad U9-12(4844.921mil,3122.087mil) on Top Layer And Pad U9-13(4865mil,3065mil) on Top Layer [Top Solder] Mask Sliver [3.811mil]
Waived by Jeremiah Dados at 11/7/2025 11:43:55 PM

Minimum Solder Mask Sliver Constraint: (3.811mil < 10mil) Between Pad U9-13(4865mil,3065mil) on Top Layer And Pad U9-2(4807.913mil,3065mil) on Top Layer [Top Solder] Mask Sliver [3.811mil]
Waived by Jeremiah Dados at 11/7/2025 11:43:55 PM

Minimum Solder Mask Sliver Constraint: (3.811mil < 10mil) Between Pad U9-13(4865mil,3065mil) on Top Layer And Pad U9-3(4807.913mil,3044.921mil) on Top Layer [Top Solder] Mask Sliver [3.811mil]
Waived by Jeremiah Dados at 11/7/2025 11:43:55 PM

Minimum Solder Mask Sliver Constraint: (3.811mil < 10mil) Between Pad U9-13(4865mil,3065mil) on Top Layer And Pad U9-4(4844.921mil,3007.913mil) on Top Layer [Top Solder] Mask Sliver [3.811mil]
Waived by Jeremiah Dados at 11/7/2025 11:43:55 PM

Minimum Solder Mask Sliver Constraint: (3.811mil < 10mil) Between Pad U9-13(4865mil,3065mil) on Top Layer And Pad U9-5(4865mil,3007.913mil) on Top Layer [Top Solder] Mask Sliver [3.811mil]
Waived by Jeremiah Dados at 11/7/2025 11:43:55 PM

Minimum Solder Mask Sliver Constraint: (3.811mil < 10mil) Between Pad U9-13(4865mil,3065mil) on Top Layer And Pad U9-6(4885.079mil,3007.913mil) on Top Layer [Top Solder] Mask Sliver [3.811mil]
Waived by Jeremiah Dados at 11/7/2025 11:43:55 PM

Minimum Solder Mask Sliver Constraint: (3.811mil < 10mil) Between Pad U9-13(4865mil,3065mil) on Top Layer And Pad U9-7(4922.087mil,3044.921mil) on Top Layer [Top Solder] Mask Sliver [3.811mil]
Waived by Jeremiah Dados at 11/7/2025 11:43:55 PM

Minimum Solder Mask Sliver Constraint: (3.811mil < 10mil) Between Pad U9-13(4865mil,3065mil) on Top Layer And Pad U9-8(4922.087mil,3065mil) on Top Layer [Top Solder] Mask Sliver [3.811mil]
Waived by Jeremiah Dados at 11/7/2025 11:43:55 PM

Minimum Solder Mask Sliver Constraint: (3.811mil < 10mil) Between Pad U9-13(4865mil,3065mil) on Top Layer And Pad U9-9(4922.087mil,3085.079mil) on Top Layer [Top Solder] Mask Sliver [3.811mil]
Waived by Jeremiah Dados at 11/7/2025 11:43:55 PM

Minimum Solder Mask Sliver Constraint: (0.268mil < 10mil) Between Pad U9-2(4807.913mil,3065mil) on Top Layer And Pad U9-3(4807.913mil,3044.921mil) on Top Layer [Top Solder] Mask Sliver [0.268mil]
Waived by Jeremiah Dados at 11/7/2025 11:43:55 PM

Minimum Solder Mask Sliver Constraint: (9.009mil < 10mil) Between Pad U9-3(4807.913mil,3044.921mil) on Top Layer And Pad U9-4(4844.921mil,3007.913mil) on Top Layer [Top Solder] Mask Sliver [9.009mil]
Waived by Jeremiah Dados at 11/7/2025 11:43:55 PM

Minimum Solder Mask Sliver Constraint: (0.268mil < 10mil) Between Pad U9-4(4844.921mil,3007.913mil) on Top Layer And Pad U9-5(4865mil,3007.913mil) on Top Layer [Top Solder] Mask Sliver [0.268mil]
Waived by Jeremiah Dados at 11/7/2025 11:43:55 PM

Minimum Solder Mask Sliver Constraint: (0.268mil < 10mil) Between Pad U9-5(4865mil,3007.913mil) on Top Layer And Pad U9-6(4885.079mil,3007.913mil) on Top Layer [Top Solder] Mask Sliver [0.268mil]
Waived by Jeremiah Dados at 11/7/2025 11:43:55 PM

Minimum Solder Mask Sliver Constraint: (9.009mil < 10mil) Between Pad U9-6(4885.079mil,3007.913mil) on Top Layer And Pad U9-7(4922.087mil,3044.921mil) on Top Layer [Top Solder] Mask Sliver [9.009mil]
Waived by Jeremiah Dados at 11/7/2025 11:43:55 PM

Minimum Solder Mask Sliver Constraint: (0.268mil < 10mil) Between Pad U9-7(4922.087mil,3044.921mil) on Top Layer And Pad U9-8(4922.087mil,3065mil) on Top Layer [Top Solder] Mask Sliver [0.268mil]
Waived by Jeremiah Dados at 11/7/2025 11:43:55 PM

Minimum Solder Mask Sliver Constraint: (0.268mil < 10mil) Between Pad U9-8(4922.087mil,3065mil) on Top Layer And Pad U9-9(4922.087mil,3085.079mil) on Top Layer [Top Solder] Mask Sliver [0.268mil]
Waived by Jeremiah Dados at 11/7/2025 11:43:55 PM

Back to top

Silk To Solder Mask (Clearance=10mil) (IsPad),(All)

Silk To Solder Mask Clearance Constraint: (9.843mil < 10mil) Between Arc (3459.449mil,2850.63mil) on Top Overlay And Pad Y1-1(3506.693mil,2858.504mil) on Top Layer [Top Overlay] to [Top Solder] clearance [9.843mil]
Waived by Jeremiah Dados at 3/4/2026 3:12:00 PM

Silk To Solder Mask Clearance Constraint: (7.32mil < 10mil) Between Arc (3770.236mil,3211.85mil) on Top Overlay And Pad R36-2(3774.37mil,3245mil) on Top Layer [Top Overlay] to [Top Solder] clearance [7.32mil]
Waived by Jeremiah Dados at 3/5/2026 5:07:27 PM

Silk To Solder Mask Clearance Constraint: (7.953mil < 10mil) Between Arc (4149.488mil,3407.598mil) on Top Overlay And Pad C11-2(4185mil,3406.378mil) on Top Layer [Top Overlay] to [Top Solder] clearance [7.953mil]
Waived by Jeremiah Dados at 3/1/2026 3:46:15 PM

Silk To Solder Mask Clearance Constraint: (5.91mil < 10mil) Between Arc (4326.413mil,2751.648mil) on Top Overlay And Pad C20-2(4297.559mil,2770mil) on Top Layer [Top Overlay] to [Top Solder] clearance [5.91mil]
Waived by Jeremiah Dados at 3/4/2026 3:12:00 PM

Silk To Solder Mask Clearance Constraint: (1.137mil < 10mil) Between Arc (5136.221mil,2192.753mil) on Top Overlay And Pad R25-2(5164.096mil,2207.789mil) on Top Layer [Top Overlay] to [Top Solder] clearance [1.137mil]
Waived by Jeremiah Dados at 3/5/2026 5:07:27 PM

Silk To Solder Mask Clearance Constraint: (7.874mil < 10mil) Between Area Fill (3321.063mil,2903.898mil) (3328.937mil,2962.953mil) on Top Overlay And Pad D1-1(3325mil,2894.055mil) on Top Layer [Top Overlay] to [Top Solder] clearance [7.874mil]
Waived by Jeremiah Dados at 3/1/2026 3:46:15 PM

Silk To Solder Mask Clearance Constraint: (4.961mil < 10mil) Between Pad C10-1(3917.992mil,2198.701mil) on Top Layer And Track (3947.559mil,2134.843mil)(3947.559mil,2197.835mil) on Top Overlay [Top Overlay] to [Top Solder] clearance [4.961mil]
Waived by Jeremiah Dados at 3/1/2026 3:46:15 PM

Silk To Solder Mask Clearance Constraint: (4.961mil < 10mil) Between Pad C10-2(3917.992mil,2125.866mil) on Top Layer And Track (3947.559mil,2134.843mil)(3947.559mil,2197.835mil) on Top Overlay [Top Overlay] to [Top Solder] clearance [4.961mil]
Waived by Jeremiah Dados at 3/1/2026 3:46:15 PM

Silk To Solder Mask Clearance Constraint: (6.965mil < 10mil) Between Pad C13-1(3925mil,2698.425mil) on Top Layer And Track (3894.413mil,2602.791mil)(3894.413mil,2717.209mil) on Top Overlay [Top Overlay] to [Top Solder] clearance [6.965mil]
Waived by Jeremiah Dados at 3/1/2026 3:46:15 PM

Silk To Solder Mask Clearance Constraint: (6.965mil < 10mil) Between Pad C13-1(3925mil,2698.425mil) on Top Layer And Track (3955.587mil,2602.791mil)(3955.587mil,2717.209mil) on Top Overlay [Top Overlay] to [Top Solder] clearance [6.965mil]
Waived by Jeremiah Dados at 3/1/2026 3:46:15 PM

Silk To Solder Mask Clearance Constraint: (5.116mil < 10mil) Between Pad C26-2(4554.783mil,2040mil) on Top Layer And Track (4523.465mil,2055.391mil)(4523.465mil,2134.609mil) on Top Overlay [Top Overlay] to [Top Solder] clearance [5.116mil]
Waived by Jeremiah Dados at 3/5/2026 5:07:27 PM

Silk To Solder Mask Clearance Constraint: (9.643mil < 10mil) Between Pad C27-1(4695mil,2684.782mil) on Top Layer And Track (4663.465mil,2670.391mil)(4663.465mil,2749.609mil) on Top Overlay [Top Overlay] to [Top Solder] clearance [9.643mil]
Waived by Jeremiah Dados at 3/4/2026 3:12:00 PM

Silk To Solder Mask Clearance Constraint: (9.643mil < 10mil) Between Pad C27-2(4695mil,2735.218mil) on Top Layer And Track (4663.465mil,2670.391mil)(4663.465mil,2749.609mil) on Top Overlay [Top Overlay] to [Top Solder] clearance [9.643mil]
Waived by Jeremiah Dados at 3/5/2026 5:07:27 PM

Silk To Solder Mask Clearance Constraint: (8.579mil < 10mil) Between Pad C30-1(4994.096mil,2756.966mil) on Top Layer And Track (5026.297mil,2672.3mil)(5026.297mil,2767.265mil) on Top Overlay [Top Overlay] to [Top Solder] clearance [8.579mil]
Waived by Jeremiah Dados at 3/1/2026 3:46:15 PM

Silk To Solder Mask Clearance Constraint: (8.579mil < 10mil) Between Pad C30-2(4994.096mil,2703.816mil) on Top Layer And Track (5026.297mil,2672.3mil)(5026.297mil,2767.265mil) on Top Overlay [Top Overlay] to [Top Solder] clearance [8.579mil]
Waived by Jeremiah Dados at 3/1/2026 3:46:15 PM

Silk To Solder Mask Clearance Constraint: (9.799mil < 10mil) Between Pad C34-1(4317.047mil,3004.409mil) on Top Layer And Track (4284.611mil,2982.594mil)(4284.611mil,3077.406mil) on Top Overlay [Top Overlay] to [Top Solder] clearance [9.799mil]
Waived by Jeremiah Dados at 3/1/2026 3:46:15 PM

Silk To Solder Mask Clearance Constraint: (8.025mil < 10mil) Between Pad C35-2(3522.59mil,2205mil) on Top Layer And Track (3556.297mil,2092.517mil)(3556.297mil,2187.483mil) on Top Overlay [Top Overlay] to [Top Solder] clearance [8.025mil]
Waived by Jeremiah Dados at 3/1/2026 3:46:15 PM

Silk To Solder Mask Clearance Constraint: (0.615mil < 10mil) Between Pad C4-1(4245mil,2425mil) on Top Layer And Track (4271.297mil,2322.517mil)(4271.297mil,2417.483mil) on Top Overlay [Top Overlay] to [Top Solder] clearance [0.615mil]
Waived by Jeremiah Dados at 3/4/2026 3:12:00 PM

Silk To Solder Mask Clearance Constraint: (Collision < 10mil) Between Pad C44-1(3258.425mil,2350mil) on Top Layer And Track (3240.433mil,2353.504mil)(3240.433mil,2416.496mil) on Top Overlay [Top Overlay] to [Top Solder] clearance [0mil]
Waived by Jeremiah Dados at 3/1/2026 3:46:15 PM

Silk To Solder Mask Clearance Constraint: (Collision < 10mil) Between Pad C44-1(3258.425mil,2350mil) on Top Layer And Track (3253.504mil,2369.567mil)(3316.496mil,2369.567mil) on Top Overlay [Top Overlay] to [Top Solder] clearance [0mil]
Waived by Jeremiah Dados at 3/1/2026 3:46:15 PM

Silk To Solder Mask Clearance Constraint: (Collision < 10mil) Between Pad C44-2(3311.575mil,2350mil) on Top Layer And Track (3253.504mil,2369.567mil)(3316.496mil,2369.567mil) on Top Overlay [Top Overlay] to [Top Solder] clearance [0mil]
Waived by Jeremiah Dados at 3/1/2026 3:46:15 PM

Silk To Solder Mask Clearance Constraint: (Collision < 10mil) Between Pad C5-2(4251.142mil,2345.866mil) on Top Layer And Track (4271.297mil,2322.517mil)(4271.297mil,2417.483mil) on Top Overlay [Top Overlay] to [Top Solder] clearance [0mil]
Waived by Jeremiah Dados at 3/1/2026 3:46:15 PM

Silk To Solder Mask Clearance Constraint: (7.486mil < 10mil) Between Pad C55-1(3340mil,2469.488mil) on Top Layer And Track (3253.504mil,2440.433mil)(3316.496mil,2440.433mil) on Top Overlay [Top Overlay] to [Top Solder] clearance [7.486mil]
Waived by Jeremiah Dados at 3/1/2026 3:46:15 PM

Silk To Solder Mask Clearance Constraint: (4.449mil < 10mil) Between Pad C55-2(3267.165mil,2469.488mil) on Top Layer And Track (3253.504mil,2440.433mil)(3316.496mil,2440.433mil) on Top Overlay [Top Overlay] to [Top Solder] clearance [4.449mil]
Waived by Jeremiah Dados at 3/1/2026 3:46:15 PM

Silk To Solder Mask Clearance Constraint: (7.984mil < 10mil) Between Pad C63-1(3555mil,2627.489mil) on Top Layer And Track (3514.413mil,2602.791mil)(3514.413mil,2717.209mil) on Top Overlay [Top Overlay] to [Top Solder] clearance [7.984mil]
Waived by Jeremiah Dados at 3/1/2026 3:46:15 PM

Silk To Solder Mask Clearance Constraint: (7.984mil < 10mil) Between Pad C63-2(3555mil,2692.511mil) on Top Layer And Track (3514.413mil,2602.791mil)(3514.413mil,2717.209mil) on Top Overlay [Top Overlay] to [Top Solder] clearance [7.984mil]
Waived by Jeremiah Dados at 3/1/2026 3:46:15 PM

Silk To Solder Mask Clearance Constraint: (8.994mil < 10mil) Between Pad C64-2(4390mil,2480mil) on Top Layer And Track (4360.389mil,2347.594mil)(4360.389mil,2442.406mil) on Top Overlay [Top Overlay] to [Top Solder] clearance [8.994mil]
Waived by Jeremiah Dados at 3/5/2026 5:07:27 PM

Silk To Solder Mask Clearance Constraint: (Collision < 10mil) Between Pad C64-2(4390mil,2480mil) on Top Layer And Track (4421.535mil,2420.391mil)(4421.535mil,2499.609mil) on Top Overlay [Top Overlay] to [Top Solder] clearance [0mil]
Waived by Jeremiah Dados at 3/4/2026 3:12:00 PM

Silk To Solder Mask Clearance Constraint: (7.984mil < 10mil) Between Pad C68-1(3470mil,2627.489mil) on Top Layer And Track (3510.587mil,2602.791mil)(3510.587mil,2717.209mil) on Top Overlay [Top Overlay] to [Top Solder] clearance [7.984mil]
Waived by Jeremiah Dados at 3/1/2026 3:46:15 PM

Silk To Solder Mask Clearance Constraint: (7.984mil < 10mil) Between Pad C68-2(3470mil,2692.511mil) on Top Layer And Track (3510.587mil,2602.791mil)(3510.587mil,2717.209mil) on Top Overlay [Top Overlay] to [Top Solder] clearance [7.984mil]
Waived by Jeremiah Dados at 3/1/2026 3:46:15 PM

Silk To Solder Mask Clearance Constraint: (7.984mil < 10mil) Between Pad C69-1(3370mil,2627.489mil) on Top Layer And Track (3329.413mil,2602.791mil)(3329.413mil,2717.209mil) on Top Overlay [Top Overlay] to [Top Solder] clearance [7.984mil]
Waived by Jeremiah Dados at 3/1/2026 3:46:15 PM

Silk To Solder Mask Clearance Constraint: (7.984mil < 10mil) Between Pad C69-2(3370mil,2692.511mil) on Top Layer And Track (3329.413mil,2602.791mil)(3329.413mil,2717.209mil) on Top Overlay [Top Overlay] to [Top Solder] clearance [7.984mil]
Waived by Jeremiah Dados at 3/1/2026 3:46:15 PM

Silk To Solder Mask Clearance Constraint: (7.984mil < 10mil) Between Pad C70-1(3285mil,2627.489mil) on Top Layer And Track (3325.587mil,2602.791mil)(3325.587mil,2717.209mil) on Top Overlay [Top Overlay] to [Top Solder] clearance [7.984mil]
Waived by Jeremiah Dados at 3/1/2026 3:46:15 PM

Silk To Solder Mask Clearance Constraint: (7.984mil < 10mil) Between Pad C70-2(3285mil,2692.511mil) on Top Layer And Track (3325.587mil,2602.791mil)(3325.587mil,2717.209mil) on Top Overlay [Top Overlay] to [Top Solder] clearance [7.984mil]
Waived by Jeremiah Dados at 3/1/2026 3:46:15 PM

Silk To Solder Mask Clearance Constraint: (6.96mil < 10mil) Between Pad Free-2(5433.219mil,2873.219mil) on Top Layer And Track (5341.968mil,2812.323mil)(5493.543mil,2812.323mil) on Top Overlay [Top Overlay] to [Top Solder] clearance [6.96mil]
Waived by Jeremiah Dados at 3/1/2026 3:46:15 PM

Silk To Solder Mask Clearance Constraint: (Collision < 10mil) Between Pad Free-2(5435mil,3365mil) on Top Layer And Track (5344.095mil,3416.457mil)(5495.669mil,3416.457mil) on Top Overlay [Top Overlay] to [Top Solder] clearance [0mil]
Waived by Jeremiah Dados at 3/1/2026 3:46:15 PM

Silk To Solder Mask Clearance Constraint: (1.984mil < 10mil) Between Pad L1-1(3911.841mil,2470.866mil) on Top Layer And Track (3869.413mil,2422.791mil)(3869.413mil,2537.209mil) on Top Overlay [Top Overlay] to [Top Solder] clearance [1.984mil]
Waived by Jeremiah Dados at 3/1/2026 3:46:15 PM

Silk To Solder Mask Clearance Constraint: (5.941mil < 10mil) Between Pad P3-1(5475mil,2160mil) on Multi-Layer And Track (5434.611mil,2077.594mil)(5434.611mil,2172.406mil) on Top Overlay [Top Overlay] to [Top Solder] clearance [5.941mil]
Waived by Jeremiah Dados at 3/4/2026 3:12:00 PM

Silk To Solder Mask Clearance Constraint: (9.599mil < 10mil) Between Pad P3-2(5475mil,2060mil) on Multi-Layer And Track (5434.611mil,2077.594mil)(5434.611mil,2172.406mil) on Top Overlay [Top Overlay] to [Top Solder] clearance [9.599mil]
Waived by Jeremiah Dados at 3/4/2026 3:12:00 PM

Silk To Solder Mask Clearance Constraint: (Collision < 10mil) Between Pad R1-1(4494.685mil,2390mil) on Top Layer And Track (4462.594mil,2374.611mil)(4557.406mil,2374.611mil) on Top Overlay [Top Overlay] to [Top Solder] clearance [0mil]
Waived by Jeremiah Dados at 3/5/2026 5:07:27 PM

Silk To Solder Mask Clearance Constraint: (6.334mil < 10mil) Between Pad R11-1(4497.602mil,3555mil) on Top Layer And Track (4527.677mil,3536.968mil)(4527.677mil,3688.543mil) on Top Overlay [Top Overlay] to [Top Solder] clearance [6.334mil]
Waived by Jeremiah Dados at 3/1/2026 3:46:15 PM

Silk To Solder Mask Clearance Constraint: (6.334mil < 10mil) Between Pad R11-1(4497.602mil,3555mil) on Top Layer And Track (4527.677mil,3536.968mil)(4657.599mil,3536.968mil) on Top Overlay [Top Overlay] to [Top Solder] clearance [6.334mil]
Waived by Jeremiah Dados at 3/1/2026 3:46:15 PM

Silk To Solder Mask Clearance Constraint: (Collision < 10mil) Between Pad R1-2(4445.315mil,2390mil) on Top Layer And Track (4429.611mil,2347.594mil)(4429.611mil,2442.406mil) on Top Overlay [Top Overlay] to [Top Solder] clearance [0mil]
Waived by Jeremiah Dados at 3/5/2026 5:07:27 PM

Silk To Solder Mask Clearance Constraint: (Collision < 10mil) Between Pad R1-2(4445.315mil,2390mil) on Top Layer And Track (4462.594mil,2374.611mil)(4557.406mil,2374.611mil) on Top Overlay [Top Overlay] to [Top Solder] clearance [0mil]
Waived by Jeremiah Dados at 3/5/2026 5:07:27 PM

Silk To Solder Mask Clearance Constraint: (8.936mil < 10mil) Between Pad R15-1(4440mil,3625mil) on Top Layer And Track (4407.323mil,3536.968mil)(4407.323mil,3688.543mil) on Top Overlay [Top Overlay] to [Top Solder] clearance [8.936mil]
Waived by Jeremiah Dados at 3/1/2026 3:46:15 PM

Silk To Solder Mask Clearance Constraint: (8.733mil < 10mil) Between Pad R15-2(4495.203mil,3625mil) on Top Layer And Track (4527.677mil,3536.968mil)(4527.677mil,3688.543mil) on Top Overlay [Top Overlay] to [Top Solder] clearance [8.733mil]
Waived by Jeremiah Dados at 3/1/2026 3:46:15 PM

Silk To Solder Mask Clearance Constraint: (7.874mil < 10mil) Between Pad R20-1(4070mil,2767.992mil) on Top Layer And Track (4054.252mil,2734.528mil)(4054.252mil,2738.465mil) on Top Overlay [Top Overlay] to [Top Solder] clearance [7.874mil]
Waived by Jeremiah Dados at 3/1/2026 3:46:15 PM

Silk To Solder Mask Clearance Constraint: (7.874mil < 10mil) Between Pad R20-1(4070mil,2767.992mil) on Top Layer And Track (4085.748mil,2734.528mil)(4085.748mil,2738.465mil) on Top Overlay [Top Overlay] to [Top Solder] clearance [7.874mil]
Waived by Jeremiah Dados at 3/1/2026 3:46:15 PM

Silk To Solder Mask Clearance Constraint: (1.965mil < 10mil) Between Pad R20-2(4070mil,2705mil) on Top Layer And Track (4044.413mil,2602.791mil)(4044.413mil,2717.209mil) on Top Overlay [Top Overlay] to [Top Solder] clearance [1.965mil]
Waived by Jeremiah Dados at 3/1/2026 3:46:15 PM

Silk To Solder Mask Clearance Constraint: (7.874mil < 10mil) Between Pad R20-2(4070mil,2705mil) on Top Layer And Track (4054.252mil,2734.528mil)(4054.252mil,2738.465mil) on Top Overlay [Top Overlay] to [Top Solder] clearance [7.874mil]
Waived by Jeremiah Dados at 3/1/2026 3:46:15 PM

Silk To Solder Mask Clearance Constraint: (7.874mil < 10mil) Between Pad R20-2(4070mil,2705mil) on Top Layer And Track (4085.748mil,2734.528mil)(4085.748mil,2738.465mil) on Top Overlay [Top Overlay] to [Top Solder] clearance [7.874mil]
Waived by Jeremiah Dados at 3/1/2026 3:46:15 PM
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

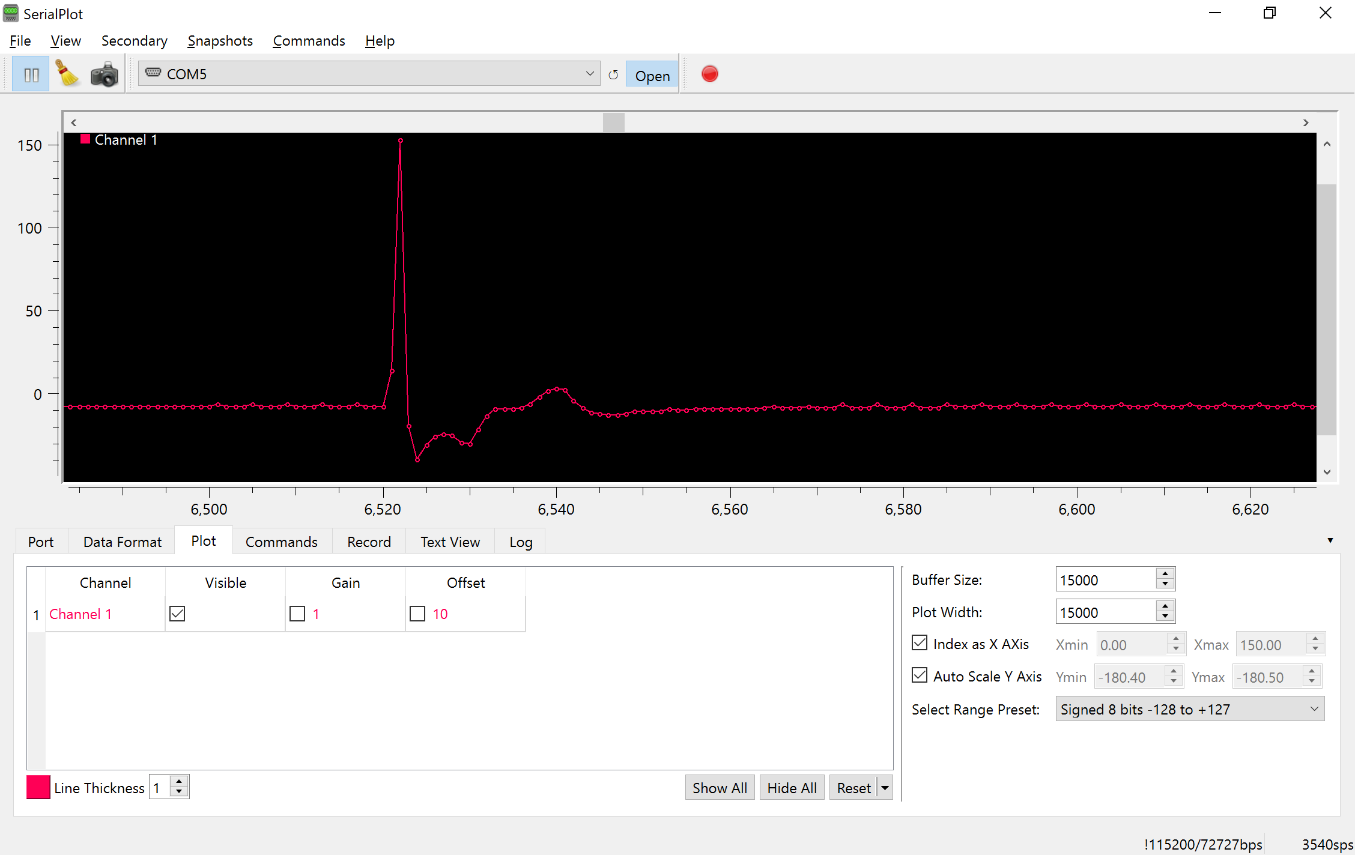
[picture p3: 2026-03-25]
experimental data/emg_big_3Vpp_1Hz_8k_sampling_rate_report_saline.PNG

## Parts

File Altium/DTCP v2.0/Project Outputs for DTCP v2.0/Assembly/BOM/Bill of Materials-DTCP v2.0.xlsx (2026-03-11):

Comment | Description | Designator | Footprint | LibRef | Quantity
C1608X5R1A106K080AC | Multilayer Ceramic Capacitors 10μF ±10% 10V X5R SMD 0603 | C1, C3, C6, C17, C18, C20, C29 | FP-C1608-080-0_1-MFG | CMP-2000-04979-3 | 7
VJ0603Y104KXJAP |  | C2, C5, C13, C14, C15, C16, C21, C30 | CAPC1608X92X38NL15T08 | CMP-2006-01211-1 | 8
CC0805MKX5R8BB226 | CAP CER 22UF 25V X5R 0805 | C4, C35 | FP-CC0805-0_2-1_45-IPC_C | CMP-03422-001497-1 | 2
C1608X5R1H105K080AB | Multilayer Ceramic Capacitors 1μF ±10% 50V X5R SMD 0603 | C7, C19, C22, C25, C26, C27, C31, C43 | FP-C1608-080-0_1-IPC_B | CMP-2000-06025-2 | 8
C0603C331J5GALTU |  | C8, C44 | CAPC1608X87X35NL15T15 | CMP-2006-03564-1 | 2
VJ0603A100KXAAC |  | C9, C45 | CAPC1608X92X38ML12T08 | CMP-2006-02012-1 | 2
C2012X5R1E475K125AB | Multilayer Ceramic Capacitors 4.7μF ±10% 25V X5R SMD 0805 | C10, C55 | FP-C2012-125-0_2-MFG | CMP-08246-004908-1 | 2
C0603C106M8PACTU | CAP CER 10UF 10V X5R 0603 | C11, C47 | FP-C0603C106M8PACTU-MFG | CMP-03020-034654-1 | 2
C0603C101K4GAC7867 | CAP CER 100PF 16V NP0 0603 | C12, C48 | FP-C0603C-CF-MFG | CMP-03020-014723-2 | 2
VJ0603Y152JXACW1BC |  | C23 | CAPC1608X95X40NL15T15 | CMP-2006-01561-1 | 1
06035C472KAZ2A |  | C24 | CAPC1608X90X35LL15T15 | CMP-2006-04440-1 | 1
GRM21BR60J107ME15K | Chip Multilayer Ceramic Capacitors for General Purpose, 0805, 100uF, X5R, 15%, 20%, 6.3V | C28, C61, C62, C63, C64, C65, C66, C67, C68, C69, C70 | FP-GRM21B-0_2-e0_2_0_7-IPC_B | CMP-06035-052658-1 | 11
VJ0603Y183KXAAC |  | C32, C33, C34 | CAPC1608X92X38ML15T08 | CMP-2006-01326-1 | 3
GRM155R71H104KE14D | Chip Multilayer Ceramic Capacitors for General Purpose, 0402, 0.10uF, X7R, 15%, 10%, 50V | C36, C37 | FP-GRM155-0_05-IPC_B | CMP-2008-04639-2 | 2
GRM1555C1H102JA01D | Chip Multilayer Ceramic Capacitors for General Purpose, 0402, 1000pF, C0G, 30ppm/°C, 5%, 50V | C38, C39, C40 | FP-GRM155-0_05-IPC_B | CMP-2008-04254-2 | 3
GRM1555C1HR40WA01D |  | C41, C42 | CAPC1005X55X25LL05T10 | CMP-1034-00010-2 | 2
150120SS75000 | Led, Red, 630 Nm, 1.9 V, 30 Ma, 60 Mcd Rohs Compliant: Yes | D1 | WL-SMCW_1206_150120xx75000 | CMP-1426-00017-3 | 1
HSMG-C150 | LED GREEN DIFFUSED 1206 SMD | D2 | FP-HSMG-C150-MFG | CMP-2000-05061-2 | 1
613010143121 |  | J1, J2, J8 | 613010143121 | CMP-1502-01419-3 | 3
SMA-J-P-H-ST-EM1 | CONN SMA JACK STR 50OHM EDGE MNT | J3, J4, J5, J6, J7 | FP-SMA-J-P-H-ST-EM1-MFG | CMP-02754-000006-1 | 5
IHLP1616BZER4R7M11 | Fixed Inductors Commercial Low DCR Series SMT 4.7uH 1.7A 105mΩ 20% | L1, L5 | FP-IHLP-1616BZ-FP_1_8545x-MFG | CMP-02424-000576-1 | 2
LQM18NNR82K00D | Multilayer Type Inductor for General Circuits, 0603 (1608), 820nH, 10%, 2.1Ω, 35mA | L2 | FP-LQM18NN_00-IPC_B | CMP-06042-016197-1 | 1
0805LS-152XJEC | 0805LS-152XJEC Coilcraft | L3 | FP-LQW21HN_00-MFG | CMP-06042-001639-1 | 1
LQW21HN1R5J00L | Wire Wound Ferrite type RF Inuctor 1.5uH ±5% 85mA 5.33Ω 0805 (2012) | L4 | FP-LQW21HN_00-MFG | CMP-06042-001639-1 | 1
DNF | Shielded Multilayer Inductor 1uH ±20% 800mA 130mΩ AEC-Q200 SMD 0805 | L14, L16, L17 | FP-MLZ2012-1_25-IPC_C | CMP-08253-000383-1 | 3
MABAES0060 | BALUN 300KHZ-200MHZ 1:1 6SMD | L15 | FP-MABAES0060-MFG | CMP-97513-000003-1 | 1
TSW-102-08-G-S-RA | 0.025" SQ Post Header, Through-hole, Right Angle, -55 to 125 degC, 2.54 mm Pitch, 2-Pin, Male, RoHS | P1, P3 | SMTC-TSW-102-08-X-S-RA | CMP-1024-00320-1 | 2
CRGCQ0603J10K | CRGCQ 0603 10K 5% | R1, R24, R26, R27, R28, R30, R35, R36, R43, R44, R61 | FP-CRGCQ0603-IPC_C | CMP-03211-009884-1 | 11
ESR03EZPF3301 | 3.3kΩ ±1% 0.25W 0603 Anti-Surge Chip Resistor AEC-Q200 | R2 | FP-ESR03-IPC_A | CMP-08839-028747-1 | 1
RN73H1JTTD1113D25 | RES 111K OHM 0.5% 1/10W 0603 | R3 | FP-CRCW0603-e3-IPC_A | CMP-2000-03018-2 | 1
RMCF0603ZG0R00 | 0Ω ±0 0.1W 0603 Thick Film Chip Resistor AEC-Q200 compliant | R4, R8, R9, R10, R13, R14, R15, R16, R17, R25, R29, R37, R41, R45, R48, R51, R53, R54, R56, R58, R59, R60, R62, R63 | FP-RMCF0603-IPC_B | CMP-26527-006412-1 | 24
CRCW060357K6FKEA | RES Thick Film, 57.6kΩ, 1%, 0.1W, 100ppm/°C, 0603 | R5, R39 | FP-CRCW0603-e3-MFG | CMP-2000-03475-2 | 2
AC0603FR-1311K3L | RES 11.3KΩ 1.00% 0.1W 0603 | R6 | FP-AC0603-IPC_C | CMP-03412-022585-2 | 1
CRCW060386K6FKEAHP | RES Thick Film, 86.6kΩ, 1%, 0.33W, 100ppm/°C, 0603 | R7, R40 | FP-CRCW0603-HPe3-MFG | CMP-02407-006337-1 | 2
DNF | 0Ω ±0 0.1W 0603 Thick Film Chip Resistor AEC-Q200 compliant | R11, R12, R18, R19, R31, R46, R57 | FP-RMCF0603-IPC_B | CMP-26527-006412-1 | 7
DNF | 100K 0.1W 1% 0603 (1608 Metric) SMD | R20, R22 | RESC0603(1608)_N | CMP-1012-00736-1 | 2
AC0805JR-0782RL | RES SMD 82 OHM 5% 1/8W 0805 | R21, R23 | FP-AC0805-MFG | CMP-03412-037249-1 | 2
CRCW08055K00FKTA |  | R32, R33 | RESC2013X50X30ML20T20 | CMP-2001-04239-1 | 2
TC33X-2-103E | Trimming Potentiometer, 10000 Ohm, -40 to 100 degC, 3-Pin SMD, RoHS, Tape and Reel | R34 | BOUR-TC33X-2_V | CMP-2100-03695-1 | 1
MCU08050C5109FP500 | RES 1.05K OHM 0.5% 1/5W 0805 | R38 | FP-MCU0805-IPC_C | CMP-02407-000931-1 | 1
CRCW06031M00JNEA | RES Thick Film, 1MΩ, 5%, 0.1W, 200ppm/°C, 0603 | R42 | FP-CRCW0603-e3-IPC_B | CMP-2000-03016-2 | 1
FCHP0402E50R0BBT1 | FCHP0402E50R0BBT1 SMD Chip Resistor, 50 Ohm, ± 0.1%, 1 W, 0402 [1005 Metric], Thin Film, High Frequency | R47 | FP-FC0402-MFG | CMP-05494-120702529-1 | 1
TFCR0805-10W-E-4222BT-1K | RES Thin Film, 42.2kΩ, 0.1%, 0.1W, 25ppm/°C, 0805 | R49 | FP-TFCR0805-IPC_A | CMP-250906-237835-1 | 1
CRCW0603220RFKEAHP | RES Thick Film, 220Ω, 1%, 0.33W, 100ppm/°C, 0603 | R50, R55 | FP-CRCW0603-HPe3-IPC_A | CMP-02407-003593-1 | 2
CRGP0805F10K | CRGP 0805 10K 1% | R52 | FP-CRGP0805-IPC_C | CMP-03211-006861-1 | 1
452406020024 | Ws-slsv_smt Mini Slide Switch Sa | SW1 | 452406020024 | CMP-03913-146831046-1 | 1
MSPM0C1104SDGS20R | 24MHz ArmÂ® CortexÂ®-M0+ MCU with 16KB flash, 1KB SRAM, 12-bit ADC 20-VSSOP -40 to 125 | U1 | DGS0020A_TEX | MSPM0C1104SDGS20R | 1
LTC3122EDE#PBF | 2.5 A Synchronous Step-Up DC/DC Converter with Output Disconnect, 12-pin SON (DE-UE-12), -40 to 125 degC, Pb-Free | U2, U11 | LT-DE-UE-12_V | CMP-0492-00369-1 | 2
TPS22810TDBVRQ1 | IC PWR SWITCH N-CHAN 1:1 SOT23-6 | U3, U10 | FP-DBV0006A-MFG | CMP-04910-000007-2 | 2
AD9850BRSZ-REEL | CMOS, 125 MHz Complete DDS Synthesizer, 10-Bit, Parallel, Serial, RS-28, 1500 Reel, Pb-Free | U4 | ADI-RS-28_N | CMP-0293-00041-1 | 1
LD39200PU33R | IC REG LINEAR 3.3V 2A 6DFN | U5 | FP-DFN6-7946637-MFG | CMP-12153-000011-1 | 1
ADS1299-4PAG | Low-Noise, 4-Channel, 24-Bit Analog-to-Digital Converter for Biopotential Measurements | U6 | QFP50P1200X1200X120-64N | ADS1299-4PAG | 1
TQP369184 | DC 6 GHz Gain Block | U7 | SOT65P210X110-6N | TQP369184 | 1
PMA3-43-1W+ | Integrated Circuit | U9 | QFN51P300X300X89-13N | PMA3-43-1W+ | 1
830207044109 | 830207044109 WE-SPXO Crystal Oscillator | Y1 | WE-SPXO_CFPS-39 | CMP-03913-116855802-1 | 1

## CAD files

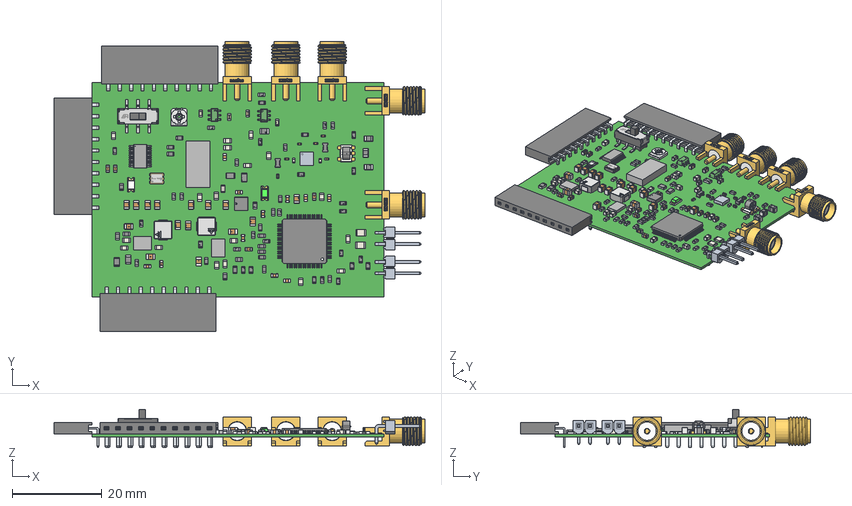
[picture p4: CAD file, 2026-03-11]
Altium/DTCP v2.0/Project Outputs for DTCP v2.0/Assembly/ExportSTEP/PCB1.step
82.6 x 64.6 x 8.54 mm
terminals x 43
top x 47
logo x 40
value x 11
Extruded x 72
Vishay logo - Copy x 4
Vishay logo x 4
SMA-J-P-H-ST-EM1 x 5
insulator x 5
pins x 3
Pads x 15
TDK_Logo x 15
housing
cover x 2
base x 2
marking
side x 40
TDK Logo x 5
Murata x 16
Base
Actuator
Sides x 4
Core x 4
Top x 4
Vishay Logo x 4
TSW-102-08-X-S-RA x 2
part number
Venkel Logo
Substrate
Leads
Coating
Logo
Ind_Murata_LQW21HN1R0J00L_eec x 8
Yageo x 2
IC_BODY x 2
IC_LEG x 6
circle x 2
Texas Instruments x 2
IC_LEG_MIR2 x 6
Cap_KEMET_C0603C272M5JACTU_eec x 6
KEMET x 2
6130xx143121_PIN x 30
STM Logo
BOUR-TC33X-2_2
Pins
Cover
terminal
Res_Rohm_ESR03EZPJ101_eec x 5
MACOM Logo abjustable
7 - Copy
7 - Copy (2)
7 - Copy (3)
Ind_Murata_LQM18NNR22K00J_eec x 4

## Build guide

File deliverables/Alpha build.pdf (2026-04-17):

## Alpha Build

Jeremiah Dados, Dmytro Stavskyi, and Luis Wong Project repository: https://github.com/jdados/dtcp
1. Current state of the project work
As of now, we have built a fully operational version of the system based on the PCB designed and ordered last semester. Currently, the system is split between 3 separate boards connected by jumper wires, as sub-systems were disconnected from each other to aid initial assembly and debugging. Nonetheless, the lab setups we have represent a vertical slice of all planned project features:

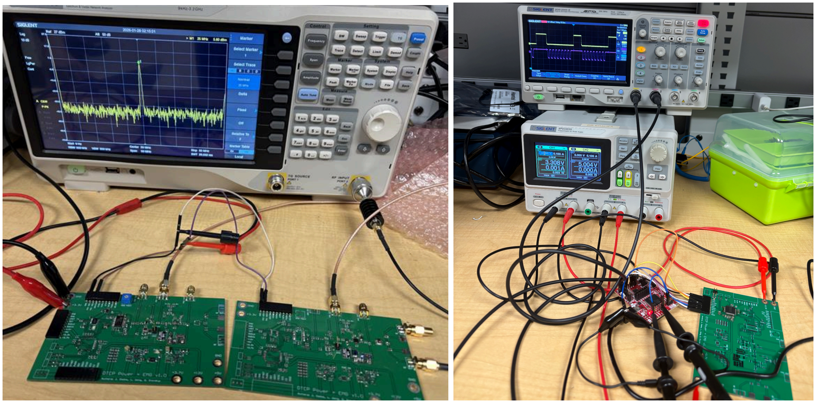
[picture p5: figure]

Setup 1 | Setup 2

Setup 1 consists of two boards powered from a DC power supply. The left one contains the MCU, DDS, and the first-stage PA, and the right one contains the second-stage PA. The RF outputs are connected to a spectrum analyzer to validate the frequency and power.

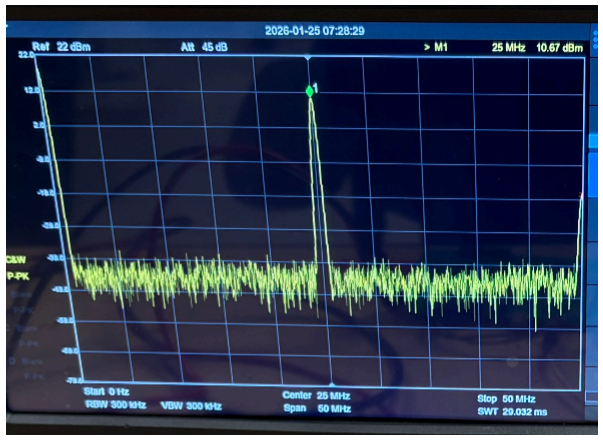
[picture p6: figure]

The most important functionality (>30 dBm output) was confirmed using a Spectrum Analyzer (here with a 20 dB attenuator in series, bringing the signal from 30.67 dBm down to 10.67 dBm)

Setup 2 is used for EMG firmware development. It consists of a Launchpad with our MCU and debugger, connected to our custom PCB that contains only the AFE circuit. Input EMG signals are supplied by a signal generator. Currently, we have tested the noise floor readings and test signal readings using the Launchpad debugger plotting the readings from memory:

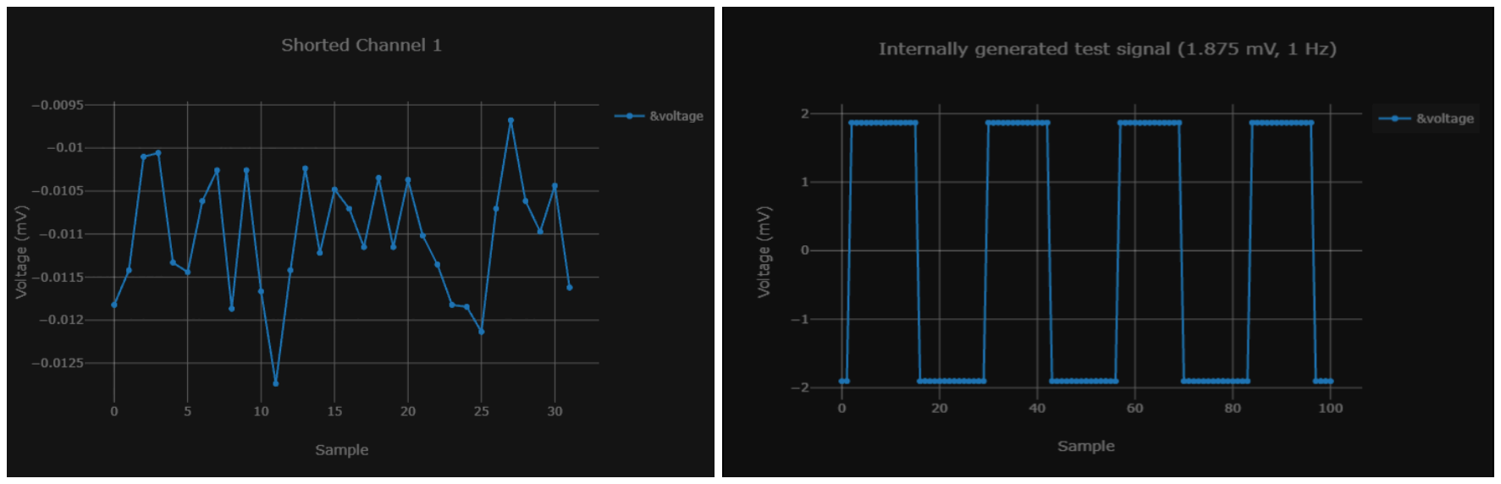
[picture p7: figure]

Initial AFE readings measuring noise floor and a test signal.
2. Usability
a. Interface
The current version of the system is composed of several partially assembled boards connected together for debugging. The MCU part of the device is interfaced with the Launchpad, which provides firmware flashing and debugging functionalities. We are also developing a UART-based interface for data acquisition.
b. Navigation and perception
Once the device is flashed with firmware, the only controls required are the power supply connections and the output power setting potentiometer. Then, the board will start transmitting power to any 50 ohm load and performing the EMG measurements.
c. Responsiveness
As of now, the firmware is not meant to be interactive and simply performs voltage readings upon device initialization. In the future, LEDs will be utilized to show device status to the user.
3. Build quality
a. Robustness and Consistency
As of now, the system is stable for over at least 15 min of continuous operation and carries out RF transmission and EMG sampling without issues. There is some heating effect present while transmitting, and it will be quantified in future experiments.
b. Aesthetic rigor
For this iteration of the design, board aesthetics were not in-scope as the ease of debugging was prioritized.
4. Vertical features
a. External interface
The interfaces established and tested with our setups are the USB-debugger-MCU digital programming interface, the signal-AFE-MCU EMG interface, and the MCU-DDS-PA-load RF output interface. All of them are carrying out all intended functionality.
b. Persistent State
Currently, EMG recording data storage is only implemented on the microcontroller. Over the following weeks, we’ll implement data movement from the microcontroller to the PC over UART.
c. Internal Systems
As of now, the interactions between all board sub-systems have been tested, errors have been identified, and with design revisions, the next PCB designed will capture all required interactions without the need for any modifications.

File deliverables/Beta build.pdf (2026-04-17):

## Beta Build

Jeremiah Dados, Dmytro Stavskyi, and Luis Wong Project repository: https://github.com/jdados/dtcp

1. Current state of the project work
Since the alpha build, we’ve been working on integrating the RF transmitter part of the design into a single board. After many hours of soldering and re-soldering, we were able to produce and validate that circuit:

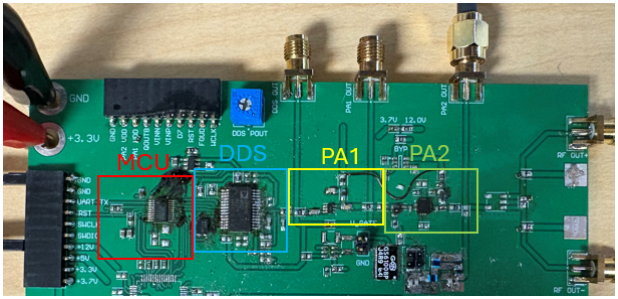
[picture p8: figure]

RF transmitter portion of the device (MCU + DDS + PA) integrated on one board

When it comes to the EMG recording circuit, most of our work has been focused on improving the firmware and circuit setup to obtain measurements in a realistic setting (no external bias, 10 mVpp AC signal):

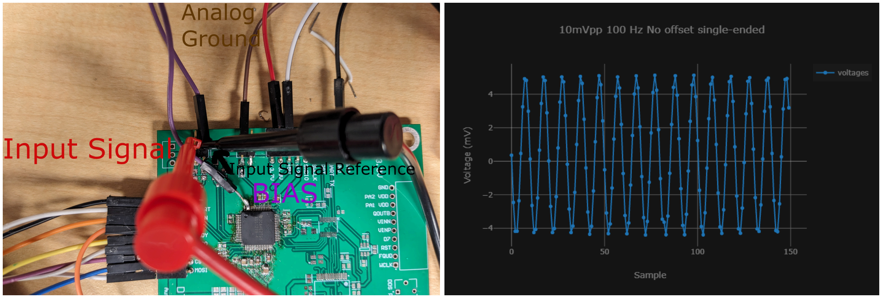
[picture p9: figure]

Current setup for data measurement with the AFE and the readings from a signal generator

Finally, we started working on the final PCB design that captures all the learnings from the first PCB, delivering a complete system free of the bugs we identified so far:

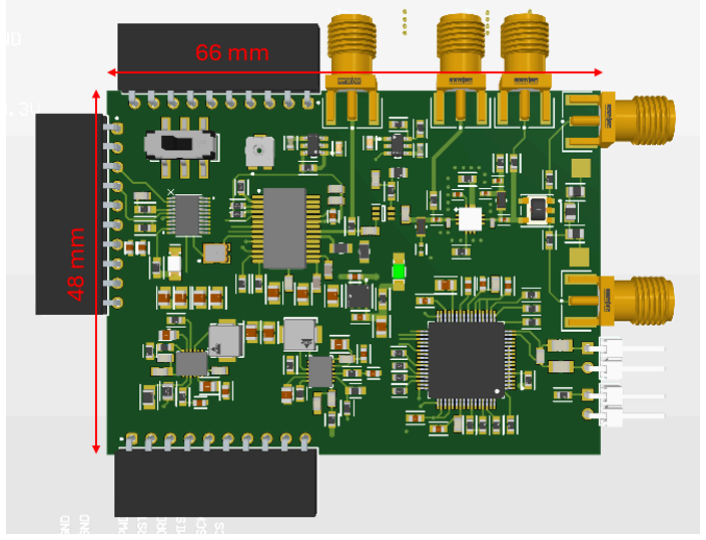
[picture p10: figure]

3D view of the new PCB layout (work in progress)

2. Usability
a. Interface
UART-based interface is being developed to be included in the beta version.
b. Navigation and perception
Once the device is flashed with firmware, the only controls required are the power supply / battery connections and the output power setting potentiometer. Then, the board will start transmitting power to any 50 ohm load and performing the EMG measurements.
c. Responsiveness
Interaction of the user with the board will be expanded in the beta version by adding a power switch for the board to turn the whole system on and off.
3. Build quality
a. Robustness and Consistency
The beta version of our circuits eliminates all the bugs of the alpha version, providing a more robust and reliable system capable of continuous operation for at least 30 min.
b. Aesthetic rigor
Board layout aesthetics will be considered in the development of the beta PCB, because it will be used for the paper figures.
4. Vertical features
a. External interface
All the external interfaces are verified and carry out functionality correctly.
b. Persistent State
Currently, EMG recording data storage is only implemented on the microcontroller. As we develop the beta device, we’ll add an option to save the recorded data on the PC.
c. Internal Systems
All the bugs and design errors have been identified and will be eliminated in the PCB design process for the beta device.

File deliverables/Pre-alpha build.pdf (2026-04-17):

## Pre-alpha build

Jeremiah Dados, Dmytro Stavskyi, and Luis Wong

### 1. Design effort

The design efforts spanned two weeks, with each member dedicating 20 hours of work to advancing the design. The breakdown of tasks and time spent on them is shown in the table below:

| Jeremiah Dados | Luis Wong | Dmytro Stavskyi
Week | Task | Time spent (hours) | Tasks | Time spent (hours) | Tasks | Time spent (hours)
12/10/2025 -18/10/2025 | Researching HF PA solutions (literature review) | 3 | Researching HF PA solutions (literature review) | 5 | Researching EMG signals and how they are usually processed and captured | 3
| HF PA simulations: class- A | 3 | HF PA simulations: Class-A | 2 | Researching how ADS1299 and the MCU (MSPM0C1104) can interact with each other (SPI and pin connections) | 3
| Researching MCU options and creating MCU wiring diagram | 4 | Creating and presenting slideshow for PAs for weekly meeting w/ professor | 3 | Setting up Altium, examining the Altium schematics of the original prototype and setting up the library for the ADS1299 chip | 4
19/10/2025 -25/10/2025 | Researching HF PA solutions (literature review) | 3 | Researching HF PA solutions (literature review) | 7 | Synthesizing information for the and creating the weekly stakeholder presentation about the ADS characteristics | 4
| PA circuit topology design | 3 | PA circuit topology design | 3 | Researching the use of ADS1299 in EMG and other signal processing systems | 4
| MCU circuit topology design | 1 | HF PA simulations: Class-E | 3 | Preliminary EMG Recording circuit design | 2
| Preliminary PCB design | 3

Table 1: Work breakdown and time commitments per team member a. System architecture design (Jeremiah)
Overview
The following diagram shows the system architecture we decided on:

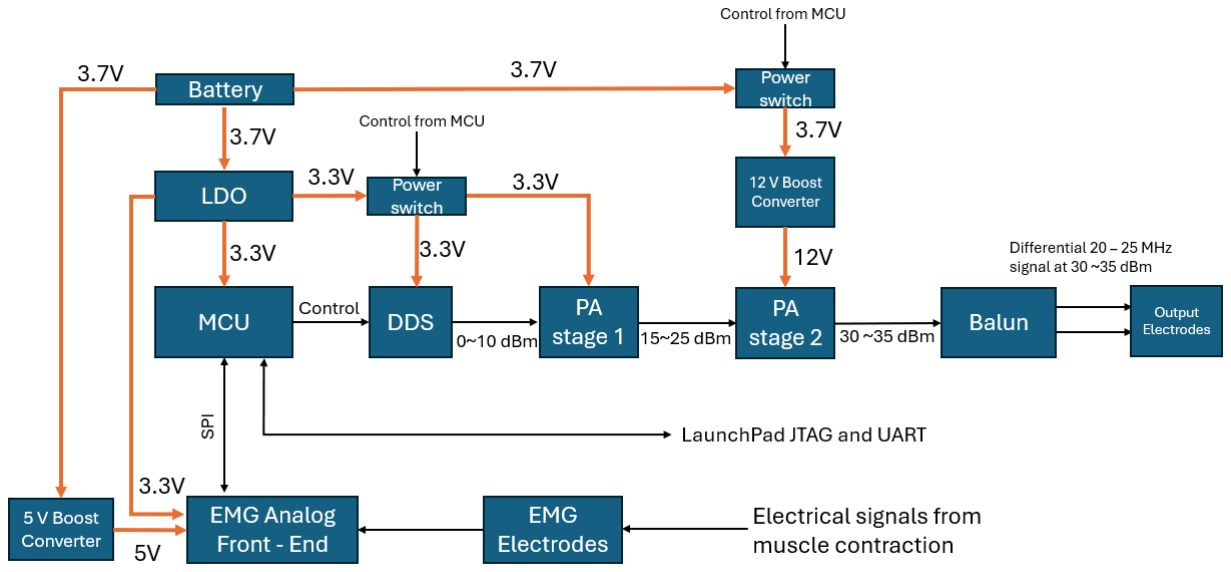
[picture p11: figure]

Figure 1: System architecture.

The design constraints received from Dr. Khalifa were the following:
- The device has to use a thin 3.7 V Li-ion battery and be able to withstand at least several hours of continuous operation without charging.
- The output signal will be differential, at 20 - 25 MHz and pulsed at 1 ms / s, with at least 1W and preferably 2W output power.
- The frequency needs to be software-adjustable.
- The output power needs to be software or hardware-adjustable (potentiometer/switch).
- The PCB cannot exceed 70 mm x 50 mm dimensions.
Therefore, all the internal system architecture components needed to be carefully chosen by us based on the literature review and previous experience. All part searches were performed using Digikey and Mouser Electronics searches.

RF Signal Generation
Review of electronic RF signal generator ICs available on the market revealed that a DDS would be the best solution based on how easy it is to digitally tune its output frequency. Other options were rejected for the following reasons:
- VCO: lower output power (below 0 dBm), harder frequency control, fewer options available in the HF band.
- Crystal oscillators: no frequency control, not designed for RF signal generation.

After a careful search of available DDS options, AD9850 was chosen due to its ability to deliver signals up to 40 MHz, with theoretical output power up to 13 dBm:

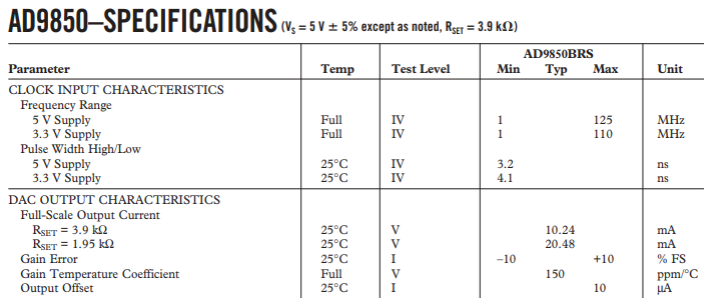
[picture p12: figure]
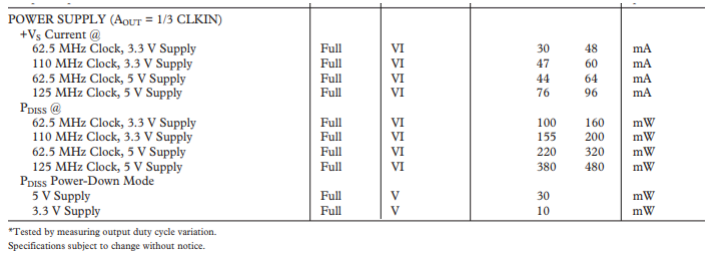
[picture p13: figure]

Figure 2: DDS output power, voltage supply, and power consumption characteristics. Source: Analog Devices (https://www.analog.com/media/en/technical-documentation/data-sheets/ad9850.pdf)

The output power was calculated based on the maximum output current and a 50-ohm load:

P = I

2R = (20. 48 mA)

2
* 50 oℎm = 0. 021 W = 13. 22 dBm

The power consumption of around 60 mA would significantly shorten the battery life if the DDS were powered on all the time. Because of that, a power switch will be used by the microcontroller to turn off the DDS during the periods of time when power transmission is not needed.

Power switching
The part choice criteria for the power switch were as follows:
- 0 ~ 12 V input and output voltages

- >2A output current
- Simple to use

After a Digikey and Mouser search, TPS22810-Q1 was chosen as the most promising candidate based on its datasheet specs combined with the simplicity of use:

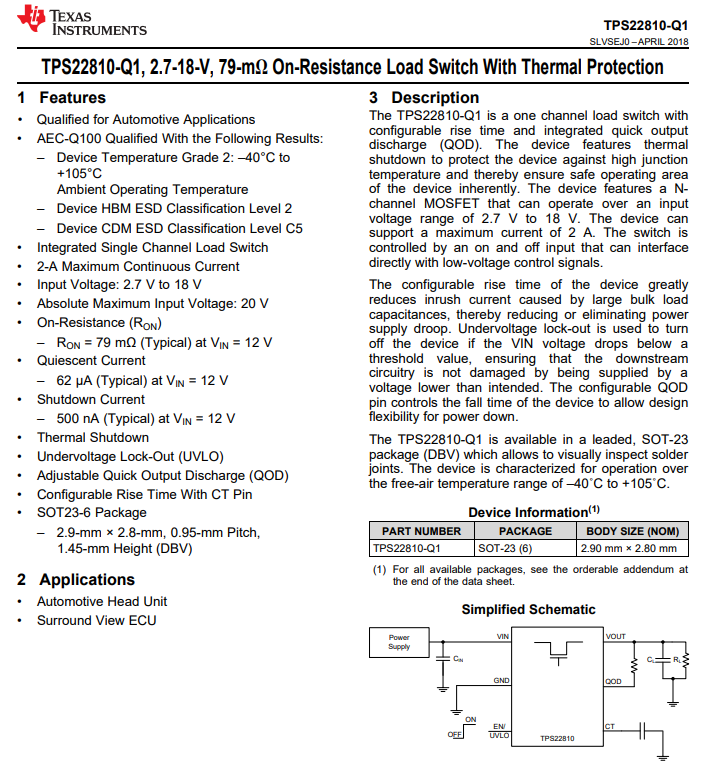
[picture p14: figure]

Figure 3: The power switch chosen for the design. Source: Texas Instruments (https://www.ti.com/product/TPS22810-Q1/part-details/TPS22810TDBVRQ1)

Power amplification
It is understood that the real output power of the DDS on the PCB might be less than the theoretical value. Because of that, the PA was designed to work with input signals as low as 5 dBm. Different topologies, such as Class-A and Class-E, were considered in the design process. The design is described in-depth in section 1b of this document.

EMG recording
The choice of the AFE (analog front-end) chip was a critically important part of the design. The programming interface, sampling rate, amplifier bandwidth, and other signal processing factors were considered. The design is described in depth in section 1c of this document.

Microcontroller
When trying to find a suitable microcontroller for this embedded system, the main criteria of the search were the following:
- Minimal external circuitry needed for programming and operation.
- Minimal part cost.
- Minimal current consumption.
- Sufficient number of GPIO pins to support DDS programming, communication with the AFE, and control of power switches.
The search was conducted among Texas Instruments ARM-based microcontrollers. That family of devices was chosen due to our familiarity with TI firmware development environments and evaluation platforms. Ultimately, the MSPM0C1104 device was chosen due to its small footprint and minimal external circuits required, as shown on its evaluation board schematic:

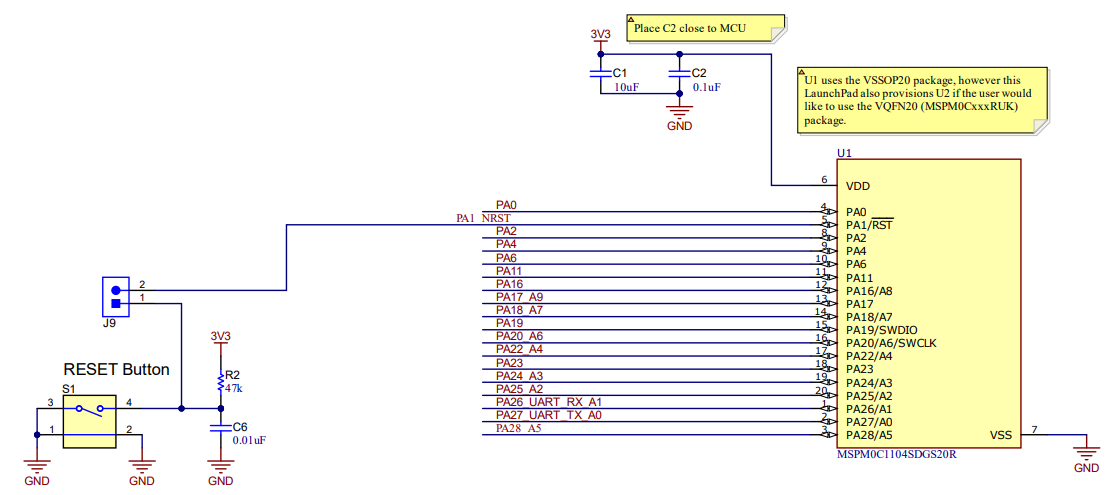
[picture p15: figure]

Figure 4: MSPM0C1104 requires only 4 external passive components to operate. Source: Texas Instruments (https://www.ti.com/tool/LP-MSPM0C1104#design-files)

Furthermore, only 3 pins (SWCLK, SWDIO, NRST) with no external ICs on board would be needed to program the device using a LaunchPad.
The microcontroller datasheet was used to verify that it can be powered directly from the battery or through a 3.3V LDO (preferred), and the expected current consumption is below 3 mA:

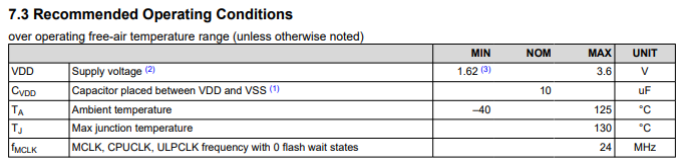
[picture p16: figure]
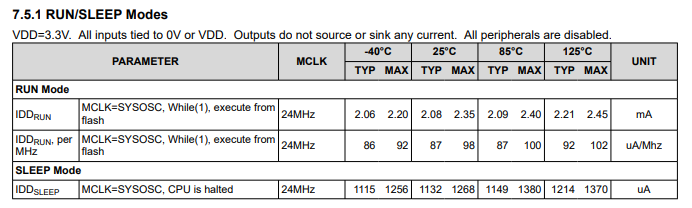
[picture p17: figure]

Figure 5: Electrical characteristics of MSPM0C1104. Source: Texas Instruments (https://www.ti.com/tool/LP-MSPM0C1104#design-files)

After choosing the microcontroller, its connections with other ICs were planned out to make sure there are enough GPIO pins for the design:

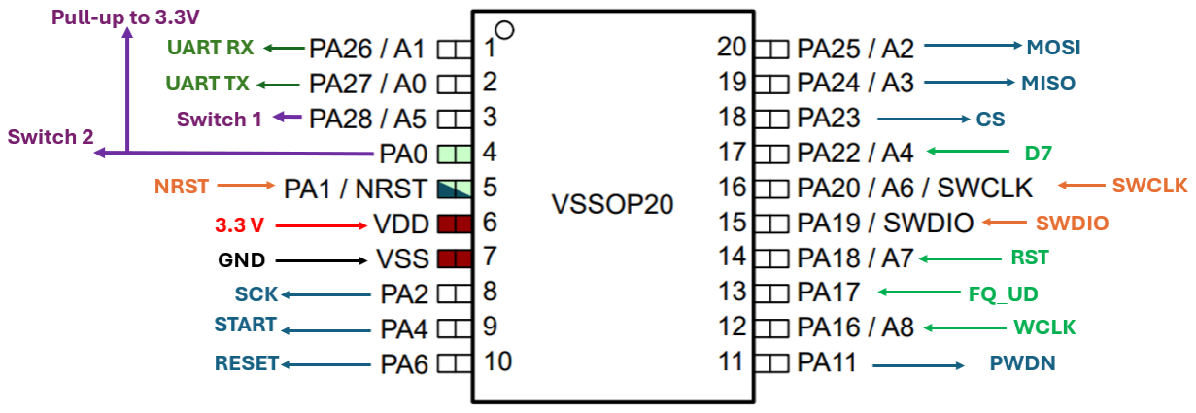
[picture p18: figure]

Figure 6: Pin assignments on the microcontroller

The dark green pins are used for UART communications, the purple are used for power switching, the orange are used for JTAG / flashing, the blue are used for the EMG chip, and the bright green are used for the DDS.

Power supplies
The requirements for the power circuit of the device were as follows:
- At least 2A output current limit for all power ICs
- LDO needed to drop 3.7V to 3.3V for the MCU and EMG AFE

- Boost converters needed to obtain 5.0 V and 12.0 V from the battery for the EMG AFE and the power amplifier.

The following ICs were chosen to meet the requirements:

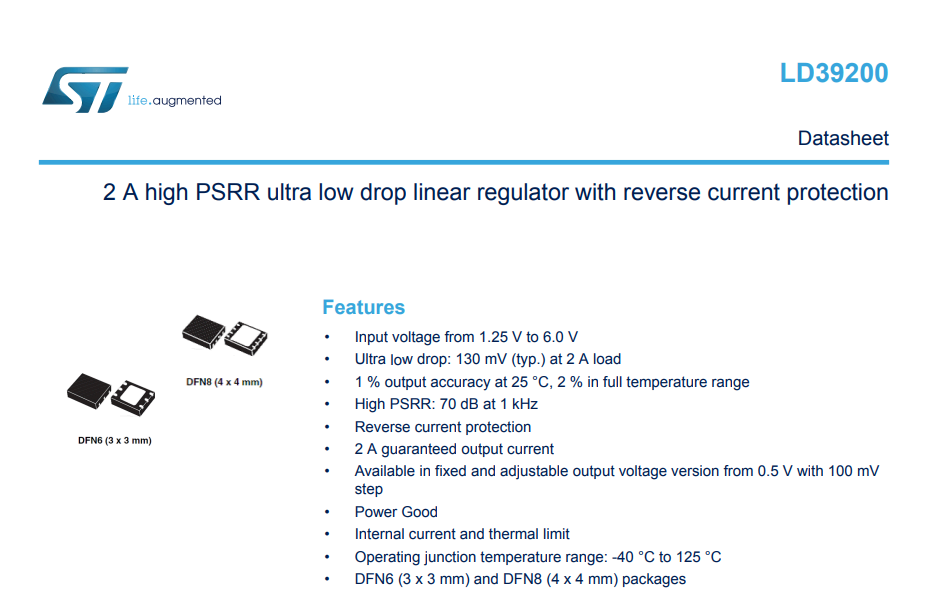
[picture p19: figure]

Figure 7: LDO chosen for the design. Source: STMicroelectronics (https://www.st.com/content/ccc/resource/technical/document/datasheet/4b/e6/2e/a4/16/04/46/9d/DM00102135.pdf/files/DM00102135.pdf/jcr:content/translations/en.DM00102135.pdf) (https://www.st.com/content/ccc/resource/technical/document/datasheet/4b/e6/2e/a4/16/04/46/9d/DM00102135.pdf/files/DM00102135.pdf/jcr:content/translations/en.D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)

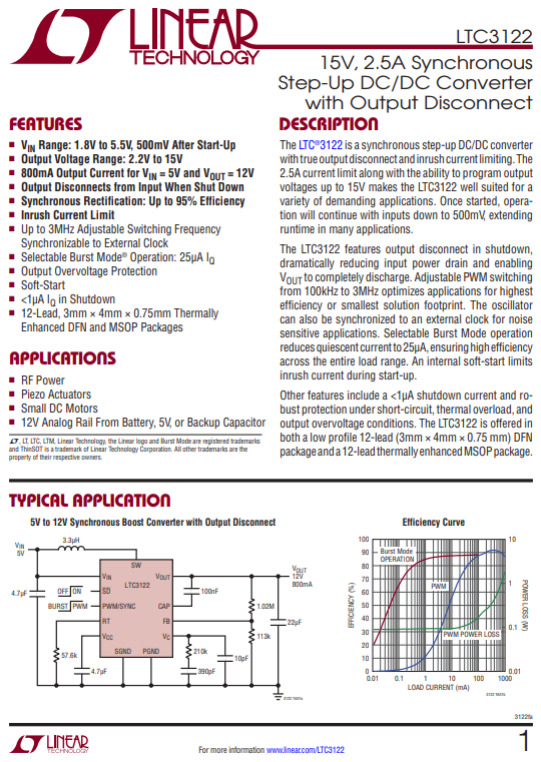
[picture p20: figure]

Figure 8: Boost converter chosen for the design. Source: STMicroelectronics (https://www.analog.com/en/products/ltc3122.html)

The LTC3122 boost converter will be used to generate both 5.0 V and 12.0 V outputs, because two instances of the chip can be placed on the PCB, each with a different voltage divider circuit setting a different output voltage.

b. PA design and simulation (Luis)

One of the main goals of the device is to present a wireless neurostimulation platform powered via Differential Tissue Coupled Powering (DTCP). This is meant to be achieved through the use of high-frequency (~ MHz) currents through conductive tissue using epidermal electrodes positioned near the implant. To this end, we need a reliable way to not only produce a high-frequency signal but also ensure that the signal has sufficient power to run the implanted devices.

I was tasked with researching and developing the PA we will need. As someone who lacks extensive experience and knowledge in designing not only PAs but also analog devices, I needed to do a lot of research in order to sufficiently propose designs to the professor for our weekly meetings.

RF (radio frequency) is a broader term, referring to any frequency used for radio communications (from e.g., tens of kHz up through MHz, GHz, etc.). While HF (high frequency) refers to a specific band within the RF umbrella between 3–30 MHz. With this information in mind, I was able to learn that what we needed to look for was information regarding RF and HF amplifiers.

Upon researching, I made use of this [1] as a primer on RF PAs due to its target audience being that of beginners and hobbyists. This allowed me to gain sufficient knowledge in order to learn about the different major amplifier classes.

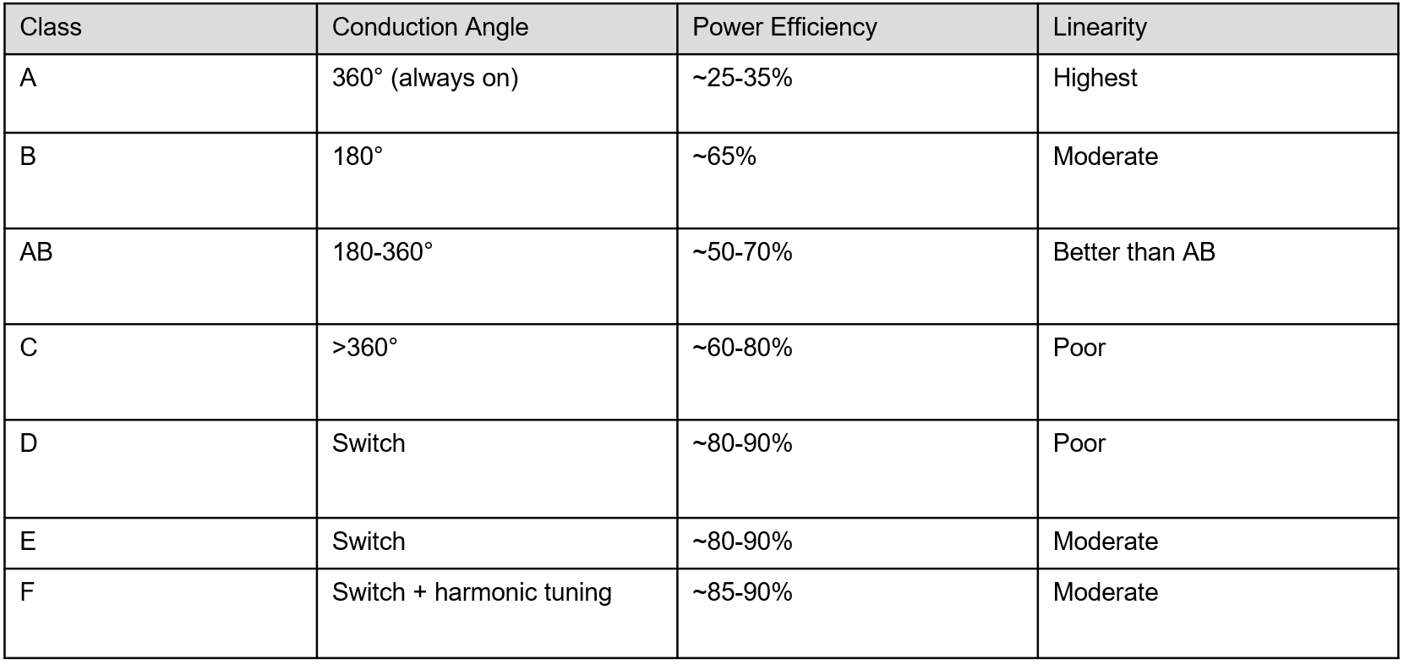
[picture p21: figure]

Figure 9: A table summarizing the characteristics of the dif erent amplifier classes [1],[3],[4].

- Linearity: refers to an amplifier’s ability to produce an output that is a faithful, scaled reproduction of its input, without unwanted distortion.

As you can see from the table, there are two main categories of amplifiers: the linear PAs (Class A, B, AB, C) and the switching PAs (Class D, E, F). Linear amplifier’s active device(s) operate in their linear (saturation) region (i.e., the output current/voltage is proportional to the input over the waveform). These are designed to preserve the waveform (amplitude and phase) and thus minimize distortion. However, linear operation means the device often has voltage across it and current through it concurrently, which leads to power dissipation (heat) and lower efficiency. A switching PA uses devices that are either fully ON or fully OFF (instead of continuously in between). Because when the device is ON, the voltage across it is low (so voltage × current ≈ small), and when it is OFF, the current through it is low (so again little dissipation), the overall power wasted is much lower, which leads to higher efficiency.

The trade‐off: switching amplifiers often require special output networks, harmonic filtering, or tuned loads, and may not support arbitrary linear modulation with high fidelity unless compensated. Linear PAs support better fidelity/linearity, but at the cost of efficiency and heat.

In our case, we do not care too much about the linearity of the waveform, just that it has a certain power (30-35 dBm) and it has a frequency ranging from 20-25 MHz. We also care about power efficiency and consumption, as our goal for this device is to run it for hours on a single battery charge. For this reason, switch PAs fit our purposes better. To that end, we decided on a Class E power amplifier design.

Why not Class D: Class D is a switching mode PA with high efficiency, but in RF applications, it has limitations: switching losses, parasitic capacitances, and device speed become more challenging at high RF frequencies. In general, it becomes very difficult to design around the limitations of Class D in HF environments.

Why not Class F: Class F uses harmonic tuning and can reach very high efficiencies, but it can add design complexity (harmonic resonators, load network complexity) and may be less attractive if we need a more straightforward PA. We would like the PCB to be relatively small; even if there was efficiency to be gained, the time and space it would take to reach that efficiency is not worth it.

Why Class E: Class E is specifically well-suited for RF power amplification in switching mode. Key reasons:
- It uses a switching element plus a tuned reactive network so that switching transitions occur under near-zero-voltage or zero-current conditions, which minimizes switching losses
- It achieves very high efficiency, which in RF power is critical (less wasted heat, smaller thermal budget, smaller size, better reliability).
- Its design is simpler (relatively) for RF switching PAs.

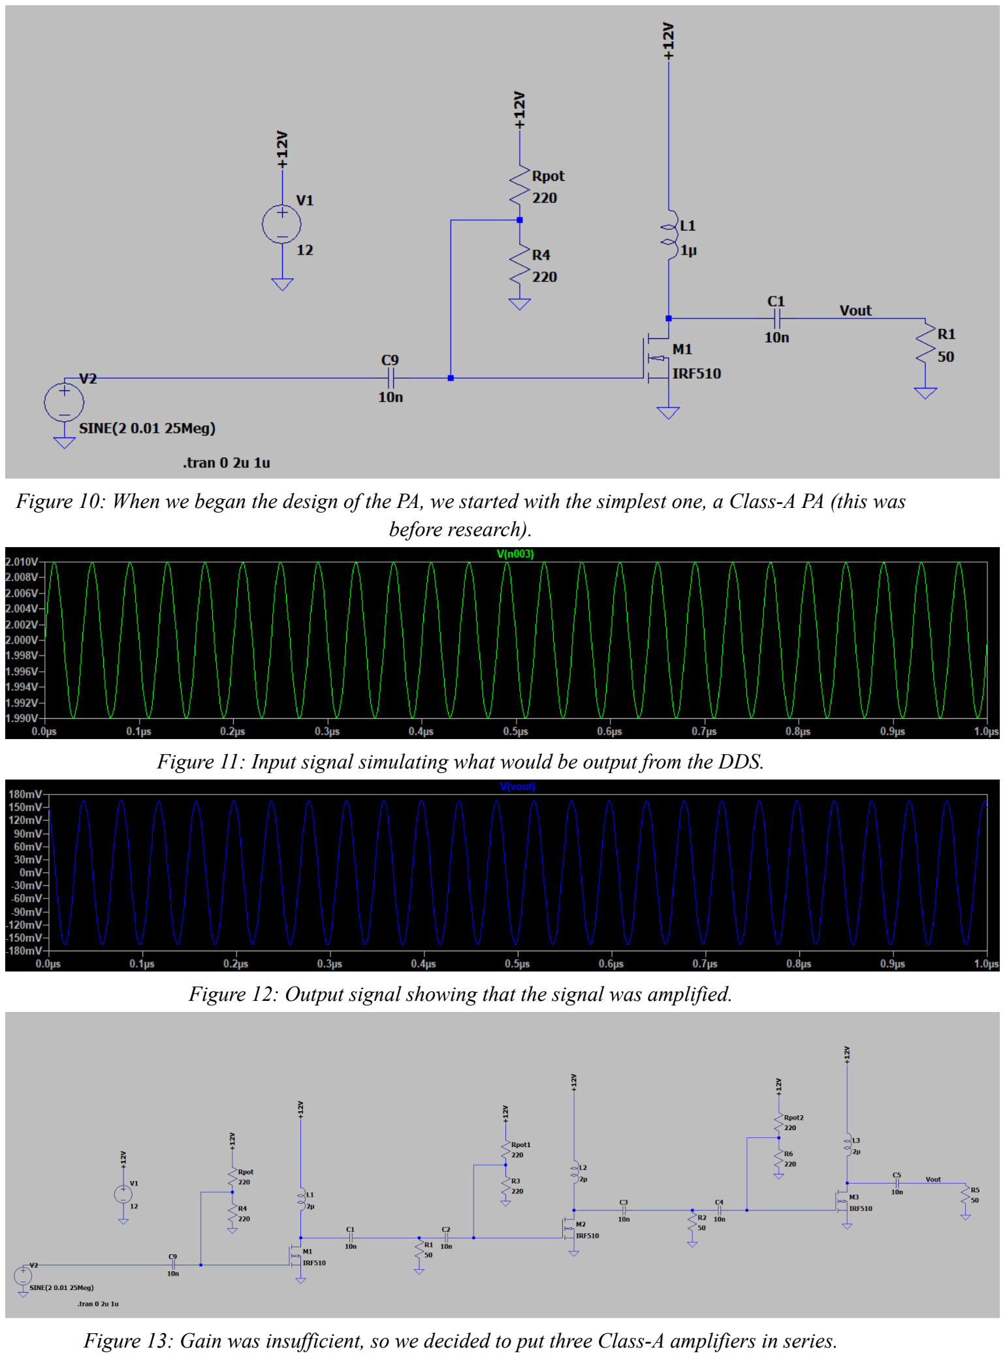
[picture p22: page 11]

Figure 10: When we began the design of the PA, we started with the simplest one, a Class-A PA (this was before research).

Figure 11: Input signal simulating what would be output from the DDS.

Figure 12: Output signal showing that the signal was amplified.

Figure 13: Gain was insuf icient, so we decided to put three Class-A amplifiers in series.

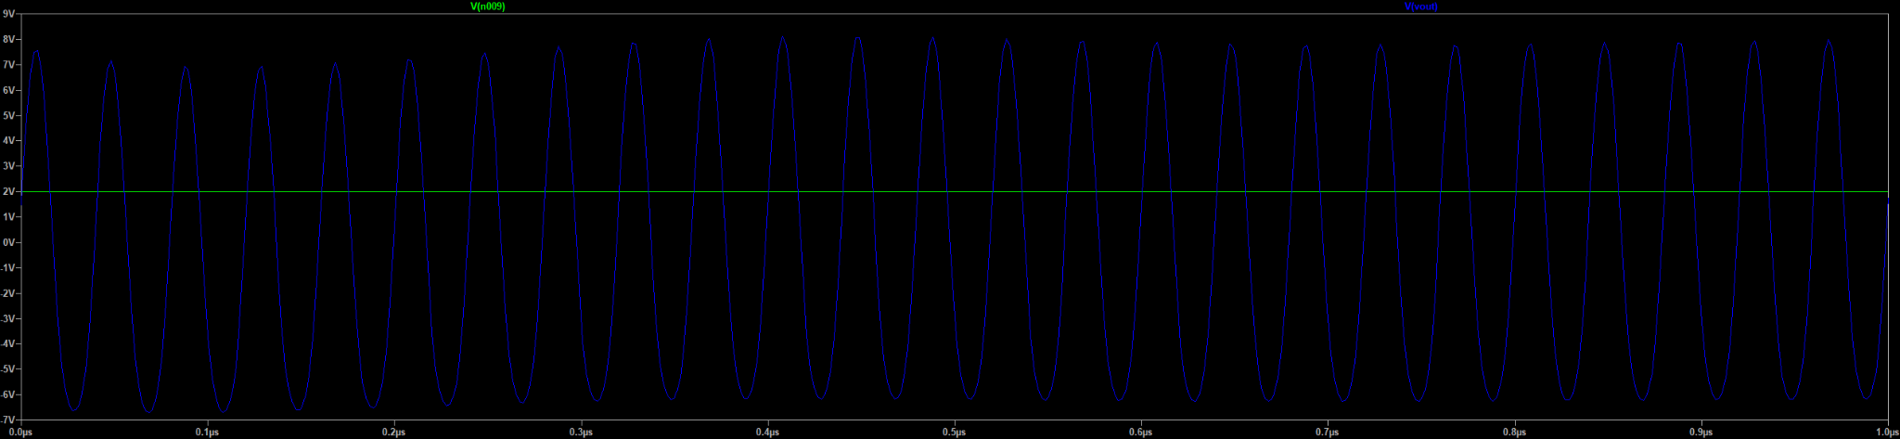
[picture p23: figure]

Figure 14: The Signal shows amplification resulting in a signal of ~14 Vpp, which is about 27 dBm. The amplitude of the signal oscillated in amplitude but with some tuning; it was dampened somewhat, but not enough to be ideal. If we want to reach the desired power, it would require too many transistors.

For this design, we drew inspiration from [2] for parts/layout and utilized a calculator (https://people.physics.anu.edu.au/~dxt103/calculators/class-e.php) based on formulas found in [5].

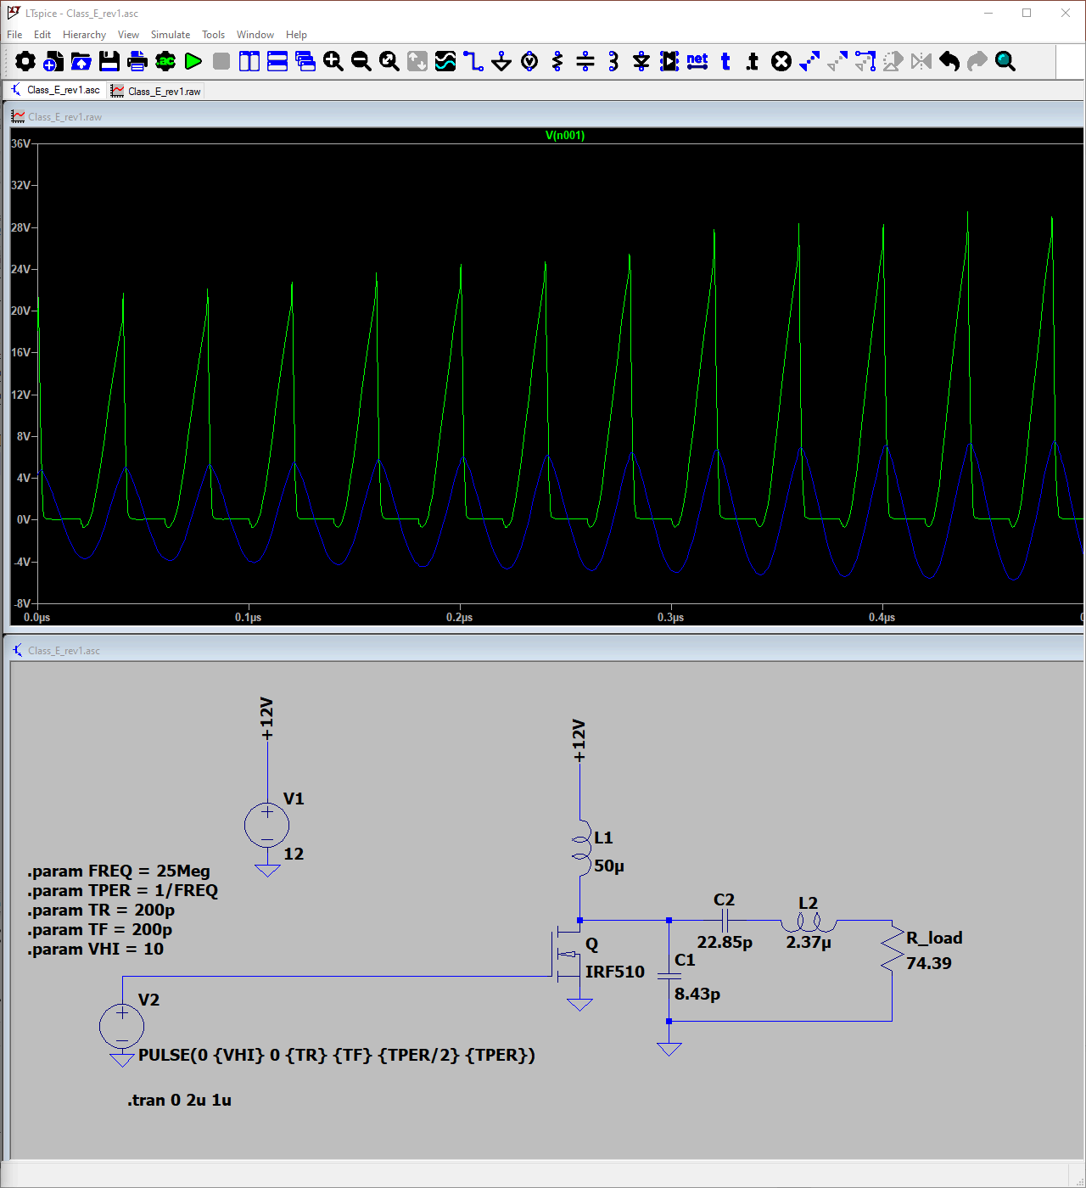
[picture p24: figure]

Figure 15: Initial attempt at designing and simulating the Class E PA. Expected a Vpp of 24 but got a Vpp of 8 instead.

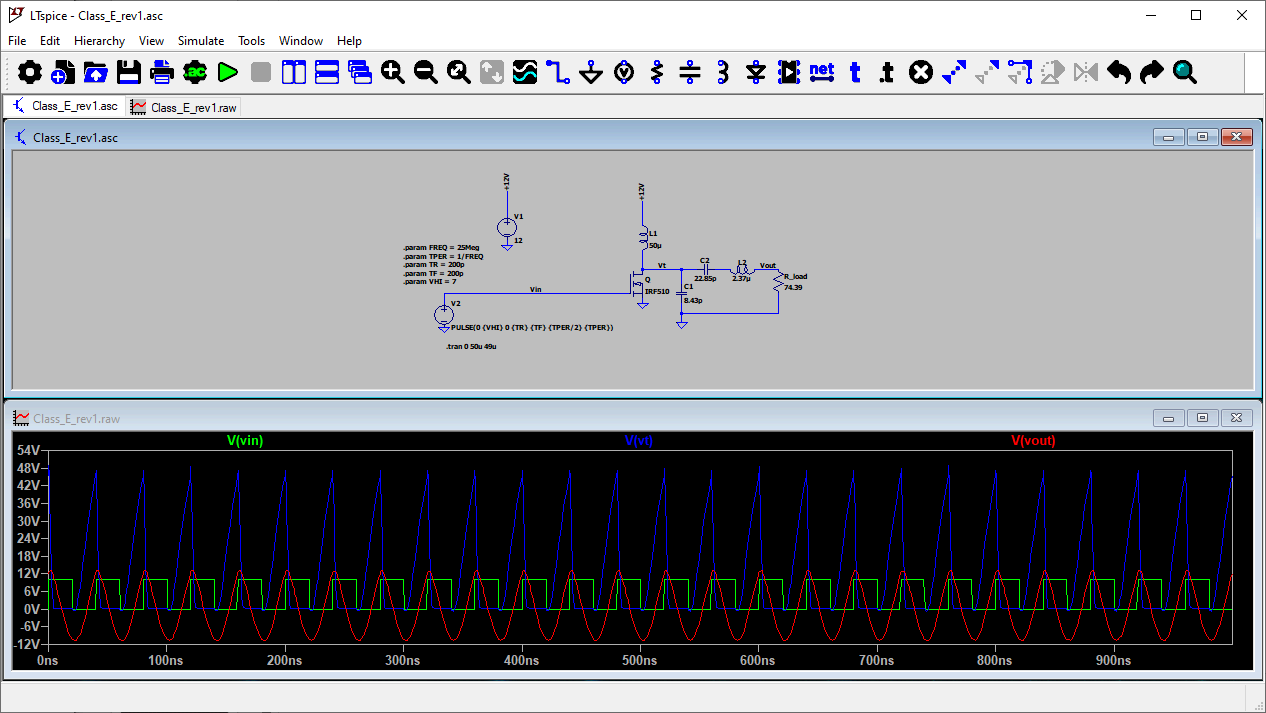
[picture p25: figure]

Figure 16: After making the simulation wait 40 microseconds, it seems like the result matched the expectation. The circuit seems to need a little time to warm up.

Figure 17: High-level view of PAs' planned design.

Here, we make use of a Balun instead of a differential PA, as it reduces the complexity of the circuit. This allows us to keep a small footprint.

Quiescent current is the current drawn by a circuit when it is powered on but not delivering any signal or load power. In switch PAs, quiescent current is very low (about 10-15 pA) or nearly zero because the transistor is off most of the time.

A power switch (like the MP5000ADQ-LF-P) is used in order to turn off the 12V boost converter, which will turn off the PA, which will further prevent any power draw from the Class E PA. A similar setup will also be utilized in the Driver/Pre-Amp and DDS stage.

A concern with the MOSFET is that its package size is too large; we can go for a smaller, more efficient option in the form of the GaN-FET, though there are concerns that this may make debugging the board more difficult, as the pins are less accessible. A good argument for using it can be found in [6]. At 13–27 MHz, device output capacitance and gate charge dominate switching loss and ringing. The paper explicitly selects an enhancement-mode GaN FET (EPC2037) for its very low capacitances and pairs it with a fast driver to achieve clean ZVS waveforms and high efficiency. This directly underpins the choice of GaN over IRF-class Si parts.

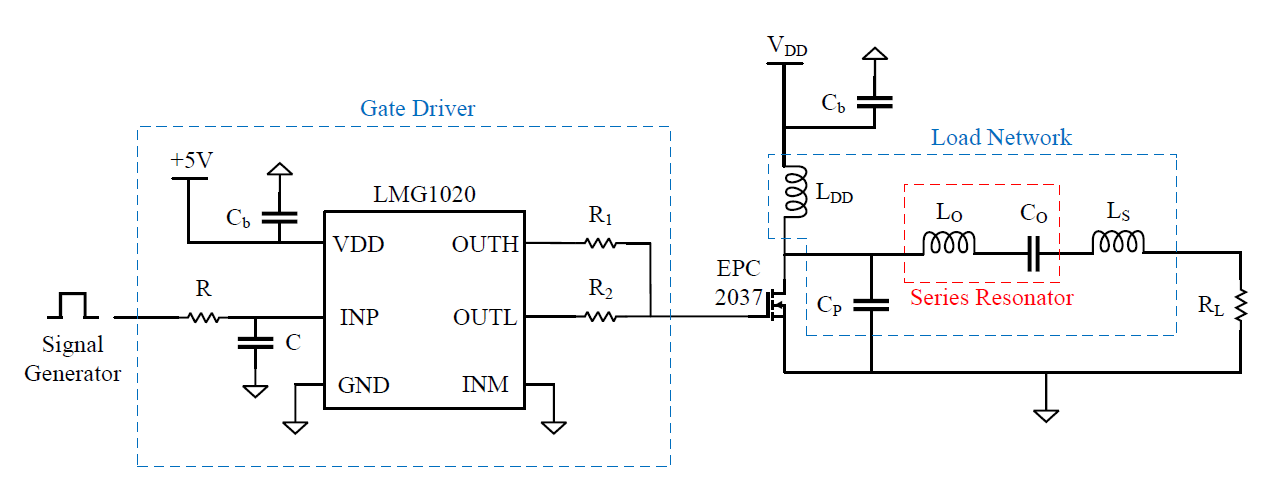
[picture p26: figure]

Figure 18: A signal generator (clock oscillator) feeds a pulse to the LMG1020 gate driver integrated with the Class E PA circuit, a good example layout for how a gate driver would drive the transistor in the next stage [6].

c. EMG design

The signal we intended to capture and record with this system is of the EMG (Electromyography) type. Specifically, we are capturing and recording the electrical activity of the animal muscles (e.g., muscle contraction).
The frequency of this type of signal is up to 500 Hz, and the amplitude ranges up to 10 mV [7].

The main criteria for the chip include minimal power consumption (since it’s a battery-powered system) and the ability to properly capture and process EMG signals (that is, adequate amplifier gain and bandwidth, sampling rate, etc.).

The AFE chip we chose for this part of the system is ADS1299-4 (4 channels).

EMG processing systems can be divided into four stages: sensing, amplifying, filtering, and ADC.

The sensing is done through analog inputs, which will be connected to electrodes (which in turn are needles connected to the animal).

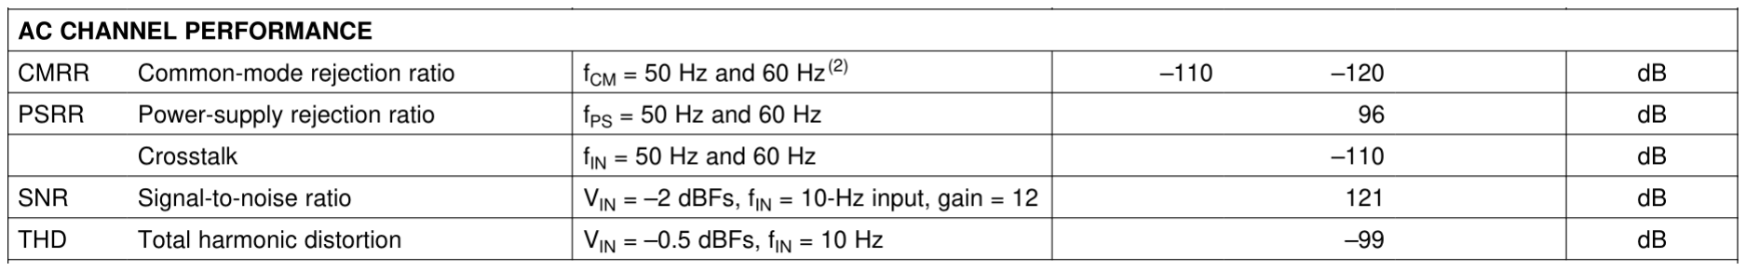
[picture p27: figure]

The device has strong general characteristics for the performance of AC channels, like low crosstalk (signals interfering with each other; specifically -110 dB for 50 Hz and 60 Hz input signals), high (im absolute magnitude) common-mode rejection ratio (CMRR; -120 dB for a particular CM frequencies) and high signal-to-noise ratio (SNR; 121 dB for a particular input),

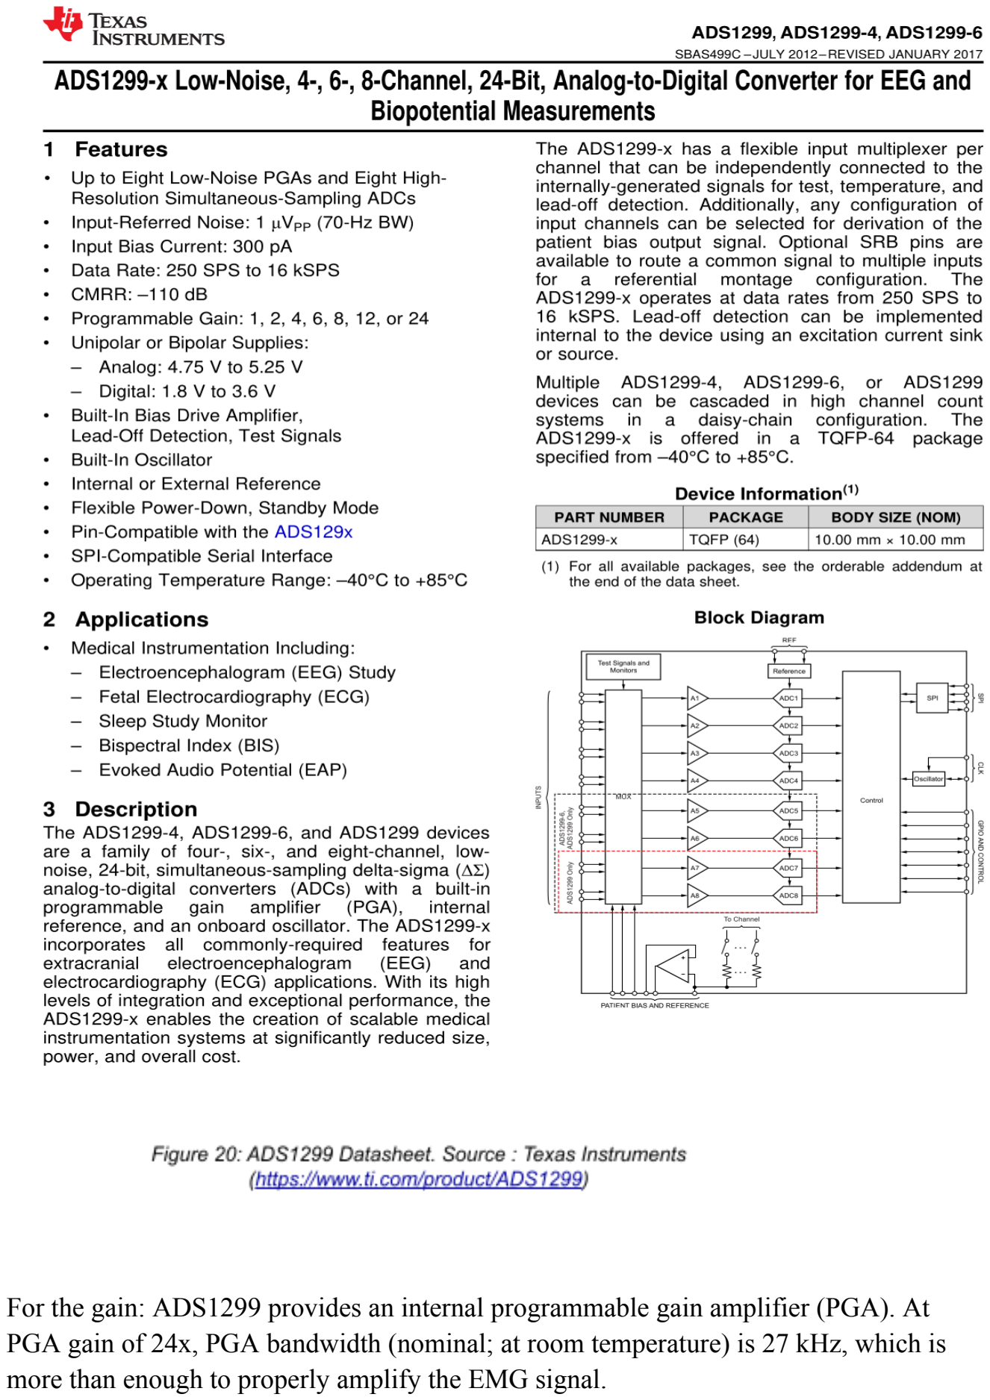
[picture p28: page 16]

For the gain: ADS1299 provides an internal programmable gain amplifier (PGA). At PGA gain of 24x, PGA bandwidth (nominal; at room temperature) is 27 kHz, which is more than enough to properly amplify the EMG signal.

Filtering will be done externally, with some form of a bandwidth filter to decouple low-frequency interferences.

The ADC:
- Resolution: 24 bits
- With an internal reference of 4.5 V, 4.5 V / 2

24 = 0.268 μV
- Possible sampling rate ranges from 250 SPS (samplings per second) to 16 kSPS (most systems use ~1000 SPS, but we may use less than that)

Power consumption (at 250 SPS):
- The quiescent power consumption of the chip is typically 10 µW.
- The measurement power consumption is typically 22 mW, and the current consumption is typically about 4.60 mA (4.06 mA for analog and 0.54 mA for digital parts)

For power supplies, the analog part of the chip will use 5 V and the digital part will use 3.3 V.

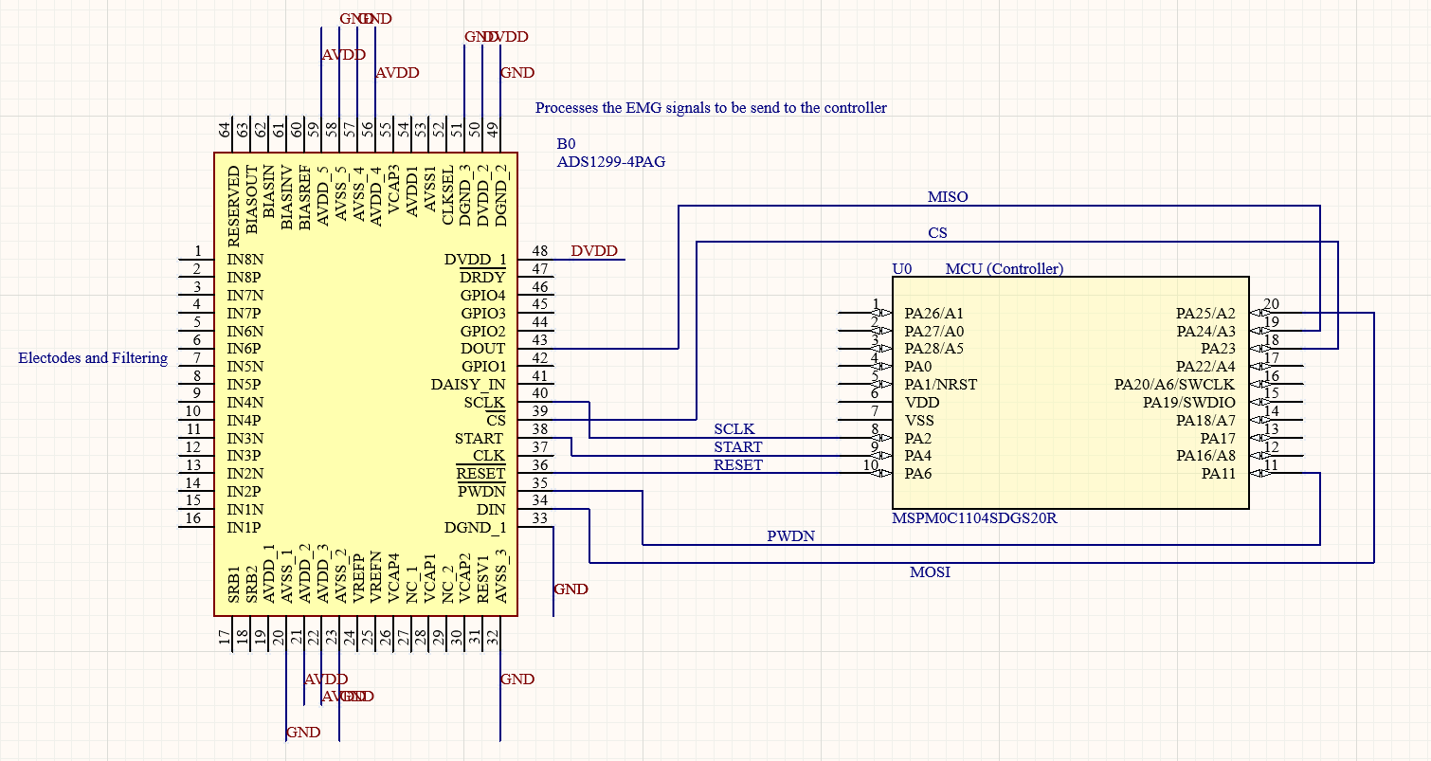
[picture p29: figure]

The chip will be interfaced with the MCU using SPI (serial communication). It can be fully programmed through SPI, though we will connect some specific signals for debugging purposes. The data conversion can be made continuous or one-shot, though the former is more fitting for the purposes of recording.

### 2. Architectural Elements

a. External Interface
There are two mechanisms of transferring external information to the microcontroller. The first one deals with flashing the device with firmware developed in the Code Composer Studio. To easily program the device from our laptops, we’ll use the MSPM0C1104 LaunchPad. The board contains an MSPM0C1104 microcontroller connected to an XDS debugger implemented on an MSP432 device through a jumper header in the middle of the board:

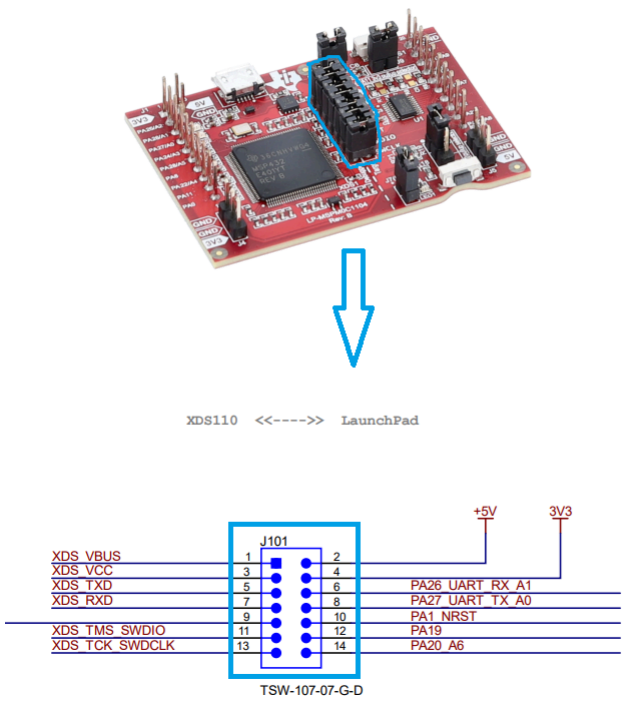
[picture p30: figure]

Figure 22: Header connecting the debug/flash circuit to an on-board MSPM0C1104 on the LaunchPad. Source: Texas Instruments (https://www.ti.com/tool/LP-MSPM0C1104#design-files)

We can remove the jumpers from the header and route the debugger circuit to the MSP microcontroller located on our custom PCB instead of the one located on the LaunchPad:

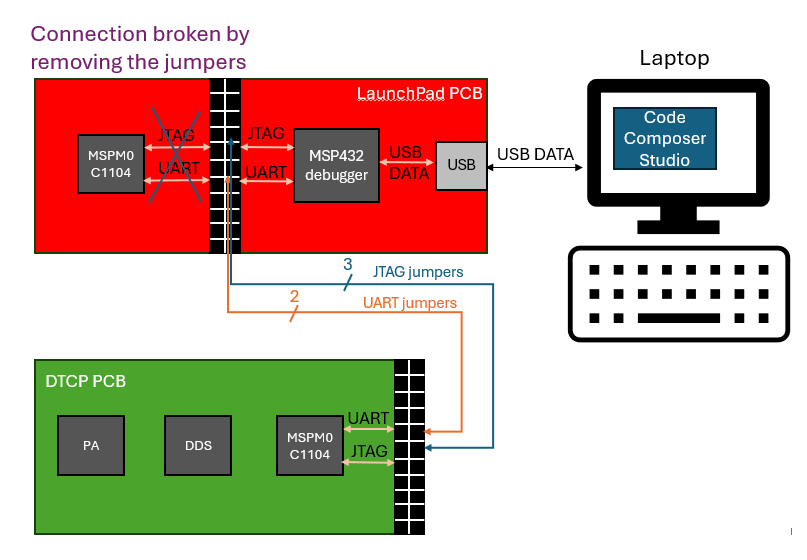
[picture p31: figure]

Figure 23: Connections between the firmware developer’s laptop, the Launchpad, and the DTCP PCB enabling programming and UART communication between the devices.

This makes the debugger treat the microcontroller on our DTCP board as if it were a part of the LaunchPad, enabling easy flashing and UART communications through the TI-developed interfaces included in the LaunchPad firmware and the Code Composer Studio firmware.

The second interface conveys the EMG voltage information from the muscle via the electrodes to the ADS1299 integrated circuit. The device amplifies the low-voltage analog signals and performs analog-to-digital conversion upon an SPI request from the microcontroller:

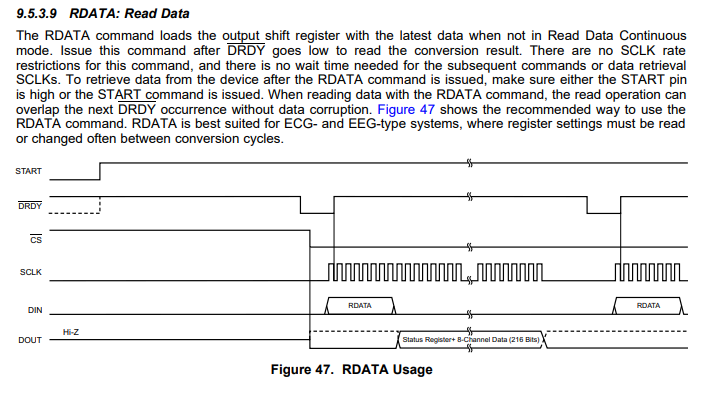
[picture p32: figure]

Figure 24: A timing diagram of reading data from the AFE using SPI. Source: Texas Instruments (https://www.ti.com/lit/ds/symlink/ads1299.pdf)

The PCB will establish the correct connections between the MSPM0C1104 and ADS1299, while the firmware will ensure the control signals, data, and clock are correctly applied or read at the right times.

b. Persistent State
The following data flow diagram shows how the EMG voltages will be collected from the external interface (electrodes) and stored persistently (in a .txt file on the user's laptop):

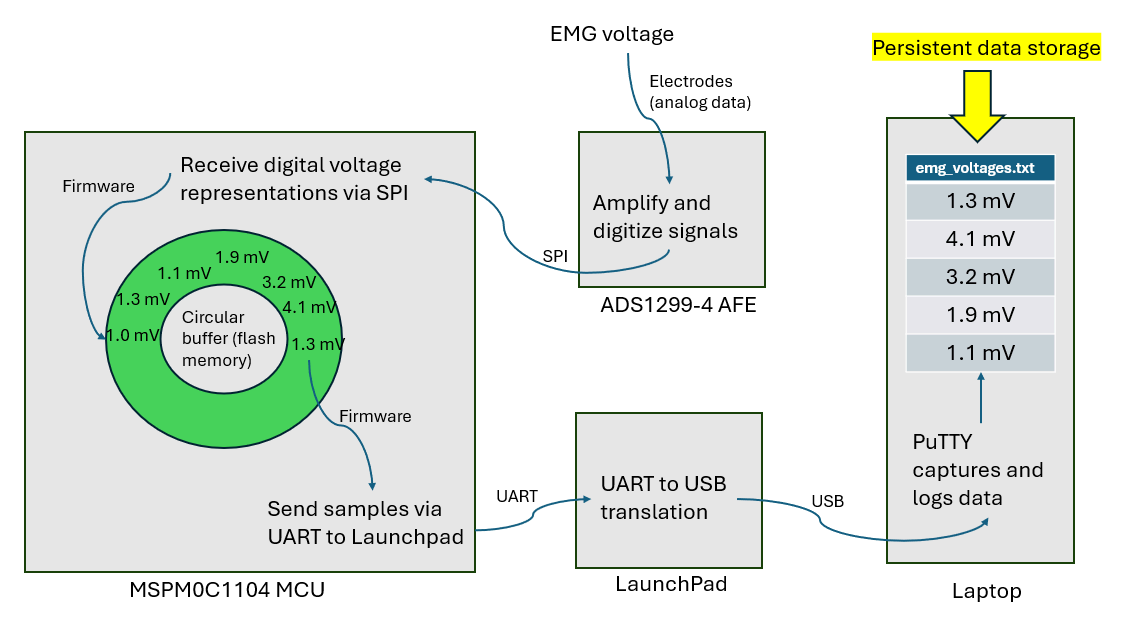
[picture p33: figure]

Figure 25: Connections between the firmware developer’s laptop, the Launchpad and the DTCP PCB enabling programming and UART communication between the devices.

The voltage samples will need to be stored in a circular buffer in device memory to not introduce sampling latency from the time needed to transmit data to the laptop through the LaunchPad. The SPI firmware interface will read the voltage samples from the ADS1299 AFE and place them in the buffer (advancing the write pointer) while the UART interface will be printing the samples to PuTTY at the same time (advancing the read pointer).

c. Internal Systems
The following flowchart shows how the data is handled by the internal systems.

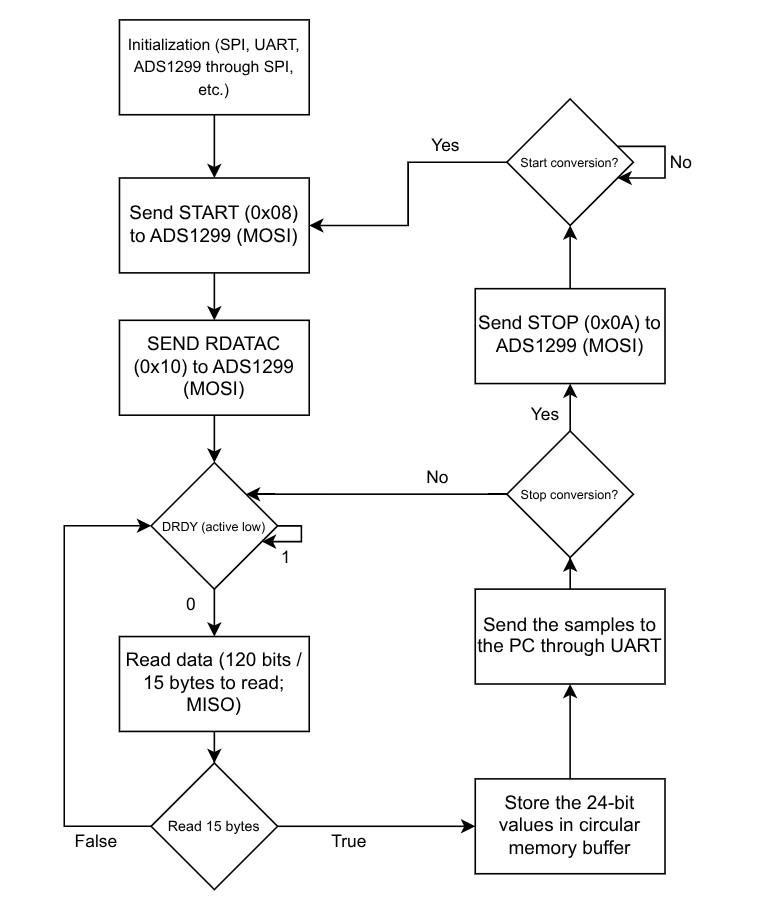
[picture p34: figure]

Figure 26: Data handling flowchart

### 3. Information Handling

a. Communication
As shown in figures 23-26, the ADS1299 microcontroller will use SPI to communicate with the AFE, and JTAG and UART to communicate with the LaunchPad. The LaunchPad will use USB serial data to communicate with Code Composer Studio and PuTTY on the user's laptop.
b. Integrity & Resilience

Because the DTCP implant power transmitter is a single-user research device, data corruption or malicious intrusion are not concerns. However, as a part of signal processing, the microprocessor will implement basic sanity checking on the received EMG data to ensure the received signals actually represent muscle activity rather than noise. Removing noise from the system is an important part of the design. The device should be isolated from 60 Hz power supply noise when it’s battery powered, but it must be ensured that when data is being sent to a laptop, that device is also using a battery rather than being connected to a power supply that might propagate noise onto the PCB.

### 4. Project Repository and Video

GitHub repository: https://github.com/jdados/dtcp
Project overview video: https://youtu.be/saHZVm3RDYI

Bibliography
[1] M. Ludens, “RF Power Amplifier Design,” ludens.cl, 2020. https://ludens.cl/Electron/RFamps/RFamps.html
[2] Texas Instruments, “HF Power Amplifier (Reference Design Guide) RFID Systems / ASP 1.) Scope,” 2004. Accessed: Oct. 21, 2025. [Online]. Available: https://e2e.ti.com/cfs-file/__key/telligent-evolution-components-attachments/00-667-00-00-00-11-91-53/appnote_5F00_trf796x_5F00_pwramp_5F00_4w.pdf (https://e2e.ti.com/cfs-file/__key/telligent-evolution-components-attachments/00-667-00-00-00-11-91-53/appnote_5F00_trf796x_5F00_pwramp_5F00_4w.pdf)
[3] S. C. Cripps, RF Power Amplifiers for Wireless Communications, 2nd ed., Norwood, MA, USA: Artech House, 2006.
[4] F. H. Raab et al., “Power amplifiers and transmitters for RF and microwave,” IEEE Transactions on Microwave Theory and Techniques, vol. 50, no. 3, pp. 814–826, Mar. 2002. doi: 10.1109/22.989965
[5] N. O. Sokal and A. D. Sokal, “Class E-A new class of high-efficiency tuned single-ended switching power amplifiers,” IEEE Journal of Solid-State Circuits, vol. 10, no. 3, pp. 168–176, Jun. 1975, doi: https://doi.org/10.1109/jssc.1975.1050582.
[6] H. Dadashzadeh, “Design and implementation of class-E power amplifiers and rectifiers for a dual-band capacitive wireless power transfer system,” Doi.org, Oct. 2025, doi: https://doi.org/10.14288/1.0406624.
[7] Bernabe Rodríguez-Tapia et al. “Myoelectric Interfaces and Related Applications: Current State of EMG Signal Processing–A Systematic Review”. In: IEEE Access 8 (2020), pp. 7792–7805. DOI: 10.1109/ACCESS.2019.2963881.

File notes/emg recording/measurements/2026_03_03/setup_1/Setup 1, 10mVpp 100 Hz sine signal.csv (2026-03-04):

Sample | Voltage (mV)
0 | -50.4747696
1 | -50.3431931
2 | -50.2825165
3 | -50.2509766
4 | -50.2266159
5 | -50.2047119
6 | -50.0717545
7 | -49.6522217
8 | -49.5338097
9 | -49.6549034
10 | -49.9073219
11 | -50.0428352
12 | -50.1719475
13 | -50.4054184
14 | -50.6141014
15 | -50.7619247
16 | -50.629364
17 | -50.3814163
18 | -50.3122635
19 | -50.2670021
20 | -50.2354698
21 | -50.2206039
22 | -50.1822548
23 | -49.8885727
24 | -49.532402
25 | -49.5319786
26 | -49.7437439
27 | -49.9585724
28 | -50.091423
29 | -50.2702446
30 | -50.482769
31 | -50.6475563
32 | -50.7241707
33 | -50.4654961
34 | -50.3001022
35 | -50.2516479
36 | -49.5330963
37 | -49.5902214
38 | -49.8324966
39 | -50.0026245
40 | -50.1236267
41 | -50.3325348
42 | -50.5515404
43 | -50.7292671
44 | -50.707901
45 | -50.4288864
46 | -50.3352165
47 | -50.2914085
48 | -50.2513123
49 | -50.2294769
50 | -50.2125816
51 | -50.0304298
52 | -49.5976868
53 | -49.522728
54 | -49.6754875
55 | -49.9208221
56 | -50.0613365
57 | -50.224247
58 | -50.4469872
59 | -50.6307487
60 | -50.7611618
61 | -50.5824509
62 | -50.3460312
63 | -50.2956772
64 | -50.2739334
65 | -50.2484283
66 | -50.2234001
67 | -50.1831474
68 | -49.8563919
69 | -49.5118408
70 | -49.5201797
71 | -49.7595711
72 | -49.9615669
73 | -50.0811844
74 | -50.2780914
75 | -50.4998436
76 | -50.675312
77 | -50.7330666
78 | -50.4692955
79 | -50.3202209
80 | -50.2571678
81 | -50.2206268
82 | -50.2040634
83 | -50.1832161
84 | -50.091198
85 | -49.687088
86 | -49.5246696
87 | -49.6099815
88 | -49.8650131
89 | -50.019455
90 | -50.1418228
91 | -50.3733444
92 | -50.5933571
93 | -50.7530289
94 | -50.6753807
95 | -50.4071617
96 | -50.3248901
97 | -50.2707596
98 | -50.2347298
99 | -50.2186394
100 | -50.1969109
101 | -49.9634666
102 | -49.5619278
103 | -49.5233727
104 | -49.7067795
105 | -49.9473763
106 | -50.0868874
107 | -50.2598076
108 | -50.4837532
109 | -50.6618156
110 | -50.7704582
111 | -50.5483437
112 | -50.3524475
113 | -50.3098488
114 | -50.2832298
115 | -50.2656403
116 | -50.2420578
117 | -50.1883087
118 | -49.8123589
119 | -49.5337868
120 | -49.5823784
121 | -49.8356705
122 | -50.0203934
123 | -50.1341782
124 | -50.3487129
125 | -50.570919
126 | -50.7375603
127 | -50.7553291

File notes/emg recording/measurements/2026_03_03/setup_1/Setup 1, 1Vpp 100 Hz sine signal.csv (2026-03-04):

Sample | Voltage (mV)
0 | -25.2315845
1 | -25.6928005
2 | -25.707058
3 | -25.0789108
4 | -24.1161633
5 | -23.4597664
6 | -23.1582661
7 | -23.2741947
8 | -23.7741642
9 | -24.450676
10 | -24.7736111
11 | -24.6354218
12 | -24.4538479
13 | -24.1194477
14 | -23.6359291
15 | -23.1850605
16 | -23.1153965
17 | -23.5077515
18 | -24.219532
19 | -25.0174713
20 | -25.3461514
21 | -25.4045963
22 | -25.1780338
23 | -24.5991459
24 | -23.8792076
25 | -23.2894363
26 | -22.987421
27 | -22.7668266
28 | -23.0671196
29 | -23.8265305
30 | -24.6383266
31 | -25.0441132
32 | -24.9869194
33 | -24.6545963
34 | -24.1680813
35 | -23.7772713
36 | -23.535532
37 | -23.4377956
38 | -23.8918362
39 | -24.5428925
40 | -25.0584621
41 | -25.2503586
42 | -25.0353737
43 | -24.305088
44 | -23.1779995
45 | -22.5364208
46 | -22.4587097
47 | -22.8972168
48 | -23.5966587
49 | -24.4513683
50 | -25.2294388
51 | -25.6266193
52 | -25.5628567
53 | -24.8276081
54 | -23.8898239
55 | -23.2855244
56 | -23.0443897
57 | -23.228199
58 | -23.7755718
59 | -24.4486427
60 | -24.6742191
61 | -24.5259056
62 | -24.3092213
63 | -23.9520683
64 | -23.459074
65 | -23.0487041
66 | -23.0611992
67 | -23.5143681
68 | -24.2735519
69 | -25.0366249
70 | -25.2888451
71 | -25.3185921
72 | -25.0261421
73 | -24.4088135
74 | -22.6067791
75 | -22.9270973
76 | -23.550663
77 | -24.3730984
78 | -25.2164745
79 | -25.7444267
80 | -25.8265858
81 | -25.3029041
82 | -24.332243
83 | -23.62187
84 | -23.254303
85 | -23.3042107
86 | -23.7523727
87 | -24.4247055
88 | -24.8405933
89 | -24.7325325
90 | -24.5772209
91 | -24.2565002
92 | -23.8036442
93 | -23.3257122
94 | -23.1839008
95 | -23.518816
96 | -24.1952152
97 | -25.0128002
98 | -25.4184761
99 | -25.5079861
100 | -25.343647
101 | -24.8094139
102 | -24.0925407
103 | -23.4692211
104 | -23.1280479
105 | -22.8836269
106 | -23.0740948
107 | -23.7995319
108 | -24.6357784
109 | -25.1119232
110 | -25.1113873
111 | -24.8111134
112 | -24.3333588
113 | -23.910408
114 | -23.6593075
115 | -23.4973583
116 | -23.8820686
117 | -24.531292
118 | -25.0870705
119 | -25.3346634
120 | -25.1848068
121 | -24.5481663
122 | -23.4167881
123 | -22.6913948
124 | -22.5322418
125 | -22.9124603
126 | -23.5726337
127 | -24.4141998

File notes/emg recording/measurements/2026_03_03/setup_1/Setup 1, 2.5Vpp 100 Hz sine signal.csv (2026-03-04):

Sample | Voltage (mV)
0 | -20.0408649
1 | -21.4294033
2 | -22.066534
3 | -21.5300007
4 | -19.8544216
5 | -17.697422
6 | -16.0236301
7 | -15.4699545
8 | -16.3570023
9 | -18.4856167
10 | -20.6506176
11 | -22.2152061
12 | -22.8203773
13 | -22.0363407
14 | -20.0671024
15 | -17.7626381
16 | -15.9174013
17 | -14.8358622
18 | -15.265564
19 | -17.306366
20 | -19.8826275
21 | -21.8357697
22 | -22.5907974
23 | -22.0065689
24 | -20.2591114
25 | -18.1558876
26 | -16.4210377
27 | -15.4468222
28 | -16.1059456
29 | -18.1131554
30 | -20.4228935
31 | -22.1179829
32 | -22.6804886
33 | -21.7385921
34 | -19.3104229
35 | -16.8896484
36 | -15.2375135
37 | -14.8304758
38 | -15.8227272
39 | -18.0453682
40 | -20.6170025
41 | -22.5144062
42 | -23.2145195
43 | -22.241087
44 | -19.9574776
45 | -17.6140575
46 | -15.8446522
47 | -15.200882
48 | -16.0646439
49 | -18.1511707
50 | -20.2339687
51 | -21.5035381
52 | -21.971323
53 | -21.2350464
54 | -19.4244061
55 | -17.2885056
56 | -15.7642813
57 | -15.4334345
58 | -16.5605679
59 | -18.7950077
60 | -20.8808002
61 | -22.327961
62 | -22.7232895
63 | -21.7161312
64 | -19.628149
65 | -17.3541946
66 | -15.6216431
67 | -14.7139874
68 | -15.4467106
69 | -17.6497498
70 | -20.2033482
71 | -21.986187
72 | -22.5252686
73 | -21.7271061
74 | -19.8525887
75 | -17.7774353
76 | -16.1343765
77 | -15.3758163
78 | -16.3085041
79 | -18.437006
80 | -20.6908703
81 | -22.2285271
82 | -22.5709515
83 | -21.3543739
84 | -18.8196144
85 | -16.484621
86 | -15.0116892
87 | -14.8141832
88 | -16.0323696
89 | -22.0874748
90 | -22.893261
91 | -22.3421097
92 | -20.510952
93 | -18.2054386
94 | -16.250082
95 | -15.0170536
96 | -15.144002
97 | -17.0010395
98 | -19.5750694
99 | -21.6857128
100 | -22.6541615
101 | -22.2892513
102 | -20.6882095
103 | -18.5766258
104 | -16.7657852
105 | -15.6072054
106 | -15.9907322
107 | -17.851862
108 | -20.1819153
109 | -22.0155525
110 | -22.78475
111 | -22.1051102
112 | -19.8352222
113 | -17.3381462
114 | -15.5388594
115 | -14.9189596
116 | -15.6750383
117 | -17.7464581
118 | -20.341898
119 | -22.3907661
120 | -23.3051472
121 | -22.6238308
122 | -20.4584293
123 | -18.0730362
124 | -16.1685257
125 | -15.3079834
126 | -15.9254465
127 | -17.8724899

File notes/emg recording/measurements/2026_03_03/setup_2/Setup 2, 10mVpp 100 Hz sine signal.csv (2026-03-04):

Sample | Voltage (mV)
0 | -26.6514797
1 | -26.8670235
2 | -27.0235863
3 | -27.0205231
4 | -26.6500492
5 | -26.560873
6 | -26.5442448
7 | -26.5370483
8 | -26.5241966
9 | -26.4951191
10 | -26.3275394
11 | -25.7786903
12 | -25.6833458
13 | -25.8581009
14 | -26.1973057
15 | -26.3620701
16 | -26.5228786
17 | -26.7934914
18 | -26.9925194
19 | -27.1257477
20 | -26.914896
21 | -26.5821056
22 | -26.5302525
23 | -26.4969521
24 | -26.4914532
25 | -26.4939346
26 | -26.4846134
27 | -26.175312
28 | -25.7472649
29 | -25.7866917
30 | -26.0338593
31 | -26.2690258
32 | -26.3744965
33 | -26.5717812
34 | -26.8338566
35 | -27.0357647
36 | -27.1313114
37 | -26.7876148
38 | -26.6068687
39 | -26.5621014
40 | -26.5125523
41 | -26.4750938
42 | -26.4510231
43 | -26.3850918
44 | -25.9034939
45 | -25.7103443
46 | -25.8543892
47 | -26.2016411
48 | -26.3794804
49 | -26.490202
50 | -26.7229767
51 | -26.9226971
52 | -27.0702744
53 | -26.9997597
54 | -26.6476822
55 | -26.5916042
56 | -26.5739269
57 | -26.5575428
58 | -26.5187664
59 | -26.1568966
60 | -26.2689362
61 | -26.423645
62 | -26.6966705
63 | -26.9089756
64 | -27.0692024
65 | -26.8507309
66 | -26.5718479
67 | -26.5268803
68 | -26.4791393
69 | -26.4396458
70 | -26.4052277
71 | -26.3812237
72 | -26.0262623
73 | -25.6550941
74 | -25.7479134
75 | -26.0521412
76 | -26.2925606
77 | -26.3970699
78 | -26.5940418
79 | -26.8226814
80 | -26.9796009
81 | -27.0229149
82 | -26.6638184
83 | -26.532711
84 | -26.5224533
85 | -26.5125065
86 | -26.502182
87 | -26.4741783
88 | -26.3590088
89 | -25.8242397
90 | -25.6551609
91 | -25.7965927
92 | -26.1450977
93 | -26.3310261
94 | -26.482893
95 | -26.7534847
96 | -26.9717999
97 | -27.1195793
98 | -26.981144
99 | -26.6093731
100 | -26.538969
101 | -26.4993668
102 | -26.4839211
103 | -26.4806366
104 | -26.4803696
105 | -26.2436371
106 | -25.753233
107 | -25.7570343
108 | -25.9730015
109 | -26.2377148
110 | -26.3510742
111 | -26.5265884
112 | -26.7941837
113 | -26.9974365
114 | -27.1349335
115 | -26.8515797
116 | -26.6210175
117 | -26.5768776
118 | -26.5232811
119 | -26.4826241
120 | -26.447916
121 | -26.4013176
122 | -25.9693813
123 | -25.6803493
124 | -25.7935295
125 | -26.1227016
126 | -26.3330154
127 | -26.4344616

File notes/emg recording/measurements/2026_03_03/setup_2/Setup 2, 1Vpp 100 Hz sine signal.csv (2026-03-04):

Sample | Voltage (mV)
0 | -37.7973366
1 | -35.4524612
2 | -32.6848183
3 | -30.7263985
4 | -30.2562218
5 | -31.3037663
6 | -33.1757584
7 | -35.6365585
8 | -37.653759
9 | -38.4278297
10 | -37.4992523
11 | -35.2532578
12 | -32.7589951
13 | -31.0831947
14 | -30.8542633
15 | -31.9664669
16 | -33.9541626
17 | -36.5705223
18 | -38.3958206
19 | -38.7524414
20 | -37.5636215
21 | -35.1495972
22 | -32.2582245
23 | -29.8990898
24 | -29.5112534
25 | -30.896595
26 | -33.5984192
27 | -36.4216728
28 | -38.4004936
29 | -38.9966354
30 | -37.9863281
31 | -35.6990051
32 | -32.7586365
33 | -30.6738091
34 | -30.344326
35 | -31.5535297
36 | -33.9535828
37 | -36.6179504
38 | -38.3678207
39 | -38.2779274
40 | -36.6302185
41 | -34.2575874
42 | -31.8397217
43 | -30.3114491
44 | -30.1941109
45 | -31.6899757
46 | -34.3753281
47 | -37.2213745
48 | -39.0104065
49 | -38.8688354
50 | -37.4188614
51 | -34.9280663
52 | -32.220295
53 | -30.4853096
54 | -30.283041
55 | -31.5288754
56 | -33.4827995
57 | -35.9754295
58 | -37.8211136
59 | -38.3308296
60 | -37.1425476
61 | -34.7792358
62 | -32.3639832
63 | -30.9107857
64 | -30.9428368
65 | -32.2260857
66 | -34.3674164
67 | -36.9430733
68 | -38.55299
69 | -38.6458511
70 | -37.2253304
71 | -34.6848526
72 | -31.7914219
73 | -29.6727753
74 | -29.5890732
75 | -31.2410965
76 | -34.0407715
77 | -36.7893295
78 | -38.5682335
79 | -38.9039307
80 | -37.6517487
81 | -35.21772
82 | -32.2919693
83 | -30.4863834
84 | -30.4320049
85 | -31.8715687
86 | -34.3973427
87 | -36.9850922
88 | -38.4961281
89 | -38.0777168
90 | -36.2779846
91 | -33.8041267
92 | -31.5030403
93 | -30.1863327
94 | -30.330759
95 | -32.0739708
96 | -34.868969
97 | -37.6351852
98 | -39.1416206
99 | -38.7196312
100 | -37.0800552
101 | -34.4625168
102 | -31.8313847
103 | -30.3233166
104 | -30.3840866
105 | -31.805769
106 | -33.8498573
107 | -36.3286743
108 | -37.9544792
109 | -38.1687012
110 | -36.732914
111 | -34.2713127
112 | -30.3294849
113 | -31.2992306
114 | -33.5471039
115 | -36.2564354
116 | -38.2218742
117 | -38.4686394
118 | -36.9960442
119 | -34.728569
120 | -32.245079
121 | -30.5308132
122 | -30.1535015
123 | -31.4022198
124 | -33.957962
125 | -36.857296
126 | -38.9049797
127 | -39.067173

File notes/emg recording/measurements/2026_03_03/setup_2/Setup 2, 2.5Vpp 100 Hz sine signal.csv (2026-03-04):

Sample | Voltage (mV)
0 | -23.9125099
1 | -17.2417507
2 | -14.8274813
3 | -17.3161316
4 | -23.7510757
5 | -31.5242043
6 | -37.7789612
7 | -40.5328865
8 | -38.7391205
9 | -32.5690193
10 | -24.2937565
11 | -17.9648838
12 | -15.6159668
13 | -17.9491501
14 | -24.2184143
15 | -31.8500443
16 | -37.71064
17 | -39.5525017
18 | -37.2523499
19 | -31.0665894
20 | -23.4913464
21 | -17.5701618
22 | -15.5132236
23 | -18.2810936
24 | -24.8869247
25 | -32.6857109
26 | -38.435318
27 | -40.29953
28 | -37.9531403
29 | -31.4907017
30 | -23.5815506
31 | -17.5921764
32 | -15.547061
33 | -17.9766197
34 | -23.9577904
35 | -31.5830517
36 | -37.5800476
37 | -39.973175
38 | -37.66185
39 | -31.2893047
40 | -23.6621914
41 | -17.9803944
42 | -16.2091579
43 | -18.7321148
44 | -25.0604286
45 | -32.6420403
46 | -38.2716675
47 | -40.2010574
48 | -37.5870438
49 | -30.8961697
50 | -22.6126556
51 | -16.5421734
52 | -14.8965206
53 | -18.1808758
54 | -25.0427952
55 | -32.7526932
56 | -38.5531654
57 | -40.6099701
58 | -38.0386505
59 | -31.2963238
60 | -23.0768204
61 | -17.3201771
62 | -15.7116022
63 | -18.8002377
64 | -25.5151615
65 | -33.0596046
66 | -38.3724251
67 | -39.512764
68 | -36.5248413
69 | -29.873703
70 | -22.3905201
71 | -16.9867153
72 | -15.6918449
73 | -19.2114792
74 | -26.2319927
75 | -33.9124794
76 | -39.065876
77 | -40.2552757
78 | -37.1574554
79 | -30.2081261
80 | -14.934516
81 | -16.6123753
82 | -22.5567589
83 | -30.3072681
84 | -36.9810677
85 | -40.4120827
86 | -39.3960495
87 | -33.8534966
88 | -25.6405678
89 | -18.7898445
90 | -15.7080927
91 | -17.2601013
92 | -23.0230465
93 | -30.6579647
94 | -37.0014763
95 | -39.5656242
96 | -37.9582558
97 | -32.3231468
98 | -24.7511272
99 | -18.3732872
100 | -15.5761166
101 | -17.5584717
102 | -23.6810989
103 | -31.503912
104 | -37.7688408
105 | -40.2861862
106 | -38.6869316
107 | -32.7805672
108 | -24.8500252
109 | -18.3670502
110 | -15.5801401
111 | -17.2989216
112 | -22.7531052
113 | -30.3609314
114 | -36.7826004
115 | -39.8808022
116 | -38.3432312
117 | -32.4953804
118 | -24.846159
119 | -18.6610641
120 | -16.1813335
121 | -18.0117741
122 | -23.8157787
123 | -31.438448
124 | -37.5470161
125 | -40.1619186
126 | -38.3175087
127 | -32.1839981

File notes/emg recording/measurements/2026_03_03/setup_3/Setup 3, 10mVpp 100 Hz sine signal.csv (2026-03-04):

Sample | Voltage (mV)
0 | -6.90954685
1 | -3.83787489
2 | -0.206603393
3 | -0.00773309963
4 | -0.00773309963
5 | -0.224148139
6 | -2.64192629
7 | -4.25336123
8 | -4.49393702
9 | -5.13424158
10 | -5.25515509
11 | -5.3143158
12 | -5.62761831
13 | -2.75937557
14 | -0.0903833956
15 | -0.502182126
16 | -4.8288064
17 | -6.49381495
18 | -1.88629532
19 | -0.0142369494
20 | -0.00780014927
21 | -0.00851534959
22 | -1.11729884
23 | -4.44635391
24 | -4.61464882
25 | -5.02157545
26 | -5.13973951
27 | -5.21434402
28 | -5.37336445
29 | -5.2340126
30 | -1.18642735
31 | -0.0254790001
32 | -1.67081892
33 | -6.47126341
34 | -5.09794521
35 | -0.568293452
36 | -0.00759899989
37 | -0.00766604999
38 | -0.1020054
39 | -2.14863944
40 | -5.67850876
41 | -3.64414501
42 | -0.248643741
43 | -0.192567587
44 | -3.77634525
45 | -6.8553257
46 | -2.79111242
47 | -0.0609707981
48 | -0.00773309963
49 | -0.00777779939
50 | -0.585368812
51 | -3.46639538
52 | -4.69186831
53 | -4.93566227
54 | -5.06676722
55 | -5.22679329
56 | -5.34497976
57 | -5.59617138
58 | -2.04936099
59 | -0.0379279479
60 | -0.858061194
61 | -5.51439333
62 | -5.97361851
63 | -1.24889565
64 | -0.00780014927
65 | -0.00777779939
66 | -0.0243167989
67 | -1.53050566
68 | -3.89473319
69 | -4.50441885
70 | -4.99211788
71 | -5.1914134
72 | -5.3221159
73 | -5.49544001
74 | -4.77688742
75 | -0.726084411
76 | -0.0403864458
77 | -2.23412824
78 | -6.61872864
79 | -4.32700443
80 | -0.318822742
81 | -0.00768839987
82 | -0.00773309963
83 | -0.193930939
84 | -2.96611309
85 | -4.84498835
86 | -4.91950274
87 | -5.02381039
88 | -5.16231346
89 | -5.40657663
90 | -5.7559514
91 | -3.20380521
92 | -0.153633893
93 | -0.334266603
94 | -4.39378643
95 | -6.70108843
96 | -2.34480548
97 | -0.031379398
98 | -0.00773309963
99 | -0.0078672003
100 | -0.751764596
101 | -3.5809617
102 | -4.56221581
103 | -4.94192028
104 | -5.21067905
105 | -5.34703636
106 | -5.41804218
107 | -5.54633093
108 | -1.59351027
109 | -0.0261047985
110 | -1.16613352
111 | -5.93826103
112 | -5.57024527
113 | -0.861860693
114 | -0.00775544951
115 | -0.00780014927
116 | -0.0601214953
117 | -2.02263021
118 | -4.41703033
119 | -4.15122175
120 | -4.88378763
121 | -5.11548996
122 | -5.30137491
123 | -5.59360123
124 | -4.43126726
125 | -0.504126608
126 | -0.0936912
127 | -3.072052

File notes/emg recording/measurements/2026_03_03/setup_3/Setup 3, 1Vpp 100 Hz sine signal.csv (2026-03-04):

Sample | Voltage (mV)
0 | -2.08731103
1 | -2.15737844
2 | -2.4261148
3 | -2.74026632
4 | -2.05517197
5 | -0.185773194
6 | -0.078515552
7 | -1.65591145
8 | -3.22950792
9 | -1.53262889
10 | -0.0583558455
11 | -0.00762134977
12 | -0.00750959944
13 | -0.174151197
14 | -1.31768882
15 | -2.1311841
16 | -2.3617692
17 | -2.49866271
18 | -2.46361804
19 | -2.42980242
20 | -2.49300838
21 | -1.01113629
22 | -0.0346871987
23 | -0.368909091
24 | -2.75861573
25 | -3.40437412
26 | -0.97591275
27 | -0.0104821492
28 | -0.00773309963
29 | -0.0120019494
30 | -0.433478236
31 | -1.27602851
32 | -1.699561
33 | -2.22731137
34 | -2.63855147
35 | -3.00746059
36 | -3.33077574
37 | -2.58285522
38 | -0.411485851
39 | -0.0307088997
40 | -1.01198554
41 | -3.08575273
42 | -1.95584846
43 | -0.130903944
44 | -0.00750959944
45 | -0.00762134977
46 | -0.0632952005
47 | -0.950210214
48 | -1.7285713
49 | -1.86352062
50 | -1.87301934
51 | -2.10724735
52 | -2.34996819
53 | -2.78172541
54 | -1.70429921
55 | -0.0550257005
56 | -0.00762134977
57 | -0.00768839987
58 | -0.19120425
59 | -1.20484376
60 | -1.80098534
61 | -2.24798512
62 | -2.63984776
63 | -2.90035939
64 | -3.23062539
65 | -3.05383682
66 | -0.887004435
67 | -0.0261718482
68 | -0.493286818
69 | -2.71266413
70 | -2.58618546
71 | -0.381179243
72 | -0.00753194978
73 | -0.00750959944
74 | -0.0185728502
75 | -0.676847339
76 | -1.68393826
77 | -1.80257213
78 | -2.05805492
79 | -2.19000936
80 | -2.4888289
81 | -2.85626292
82 | -2.36313248
83 | -0.310910851
84 | -0.0430684499
85 | -1.326249
86 | -3.27335858
87 | -1.9197979
88 | -0.121628702
89 | -0.00757664954
90 | -0.00764370011
91 | -0.124154247
92 | -1.45746577
93 | -2.2499969
94 | -2.25922728
95 | -2.49396944
96 | -2.54039025
97 | -2.4601984
98 | -2.50954747
99 | -1.26266313
100 | -0.0583334975
101 | -0.236150101
102 | -2.46889257
103 | -3.58563256
104 | -1.32048273
105 | -0.0240038987
106 | -0.00753194978
107 | -0.00766604999
108 | -0.258947074
109 | -1.2315743
110 | -1.72322965
111 | -2.27896237
112 | -2.62462735
113 | -2.97491908
114 | -3.39480829
115 | -2.87188554
116 | -0.616122425
117 | -0.0239368491
118 | -0.588788331
119 | -2.79229712
120 | -2.29170203
121 | -0.237222895
122 | -0.00742019992
123 | -0.00750959944
124 | -0.0477395989
125 | -0.9836905
126 | -1.86186671
127 | -1.9000181

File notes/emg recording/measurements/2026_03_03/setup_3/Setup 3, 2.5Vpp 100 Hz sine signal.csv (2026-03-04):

Sample | Voltage (mV)
0 | -0.0232216492
1 | -2.43445134
2 | -7.70625734
3 | -7.71890783
4 | -6.38521624
5 | -4.82489538
6 | -3.64765382
7 | -3.13449788
8 | -3.16849232
9 | -0.363790929
10 | -0.00728609972
11 | -0.00721904961
12 | -0.0747383982
13 | -1.36225486
14 | -2.52519226
15 | -2.33910632
16 | -3.21296883
17 | -4.85600662
18 | -6.97796059
19 | -9.44417095
20 | -6.43883371
21 | -0.419263631
22 | -0.197104648
23 | -3.5111177
24 | -5.20406342
25 | -1.55940413
26 | -0.0212548487
27 | -0.00724139949
28 | -0.00726374984
29 | -0.854708672
30 | -5.88607311
31 | -8.08663177
32 | -7.14352894
33 | -5.4235177
34 | -3.90315914
35 | -2.91712189
36 | -2.22934532
37 | -1.25667334
38 | -0.0350224487
39 | -1.44962096
40 | -9.48516083
41 | -10.5764666
42 | -2.94526052
43 | -0.0187292993
44 | -0.00717434986
45 | -0.0113090994
46 | -0.865257859
47 | -3.42234373
48 | -5.80583715
49 | -8.40427017
50 | -9.42995644
51 | -10.0066977
52 | -9.28215599
53 | -5.45543385
54 | -0.615943611
55 | -0.0558973476
56 | -2.39884782
57 | -6.88435841
58 | -4.00257206
59 | -0.158662647
60 | -0.00719669973
61 | -0.0071296501
62 | -0.125741094
63 | -1.76404083
64 | -2.83480692
65 | -2.86911416
66 | -3.72974563
67 | -5.36493874
68 | -7.54019642
69 | -9.77555466
70 | -5.19139099
71 | -0.176654384
72 | -0.34774363
73 | -3.99068189
74 | -4.77114344
75 | -1.0356319
76 | -0.00806834921
77 | -0.00724139949
78 | -0.0073754997
79 | -1.60919988
80 | -7.13380718
81 | -8.31585407
82 | -7.00207615
83 | -5.24413681
84 | -3.83595252
85 | -2.97000194
86 | -2.5622263
87 | -0.997391045
88 | -0.0241156481
89 | -2.31662202
90 | -10.3948059
91 | -9.74323559
92 | -1.9336772
93 | -0.0073754997
94 | -0.00721904961
95 | -0.0301054493
96 | -1.34723568
97 | -5.03525352
98 | -7.40068817
99 | -8.77617359
100 | -9.6177187
101 | -10.2472734
102 | -8.98637581
103 | -4.60680437
104 | -0.344994605
105 | -0.134435251
106 | -3.18080711
107 | -7.04223919
108 | -3.12149024
109 | -0.058422897
110 | -0.00717434986
111 | -0.00719669973
112 | -0.434662789
113 | -2.7702601
114 | -2.95978808
115 | -2.94964099
116 | -3.95979404
117 | -5.6356864
118 | -7.7779789
119 | -9.79625034
120 | -3.93545485
121 | -0.063429296
122 | -0.66451019
123 | -4.69515371
124 | -4.32756329
125 | -0.65825218
126 | -0.00724139949
127 | -0.00724139949

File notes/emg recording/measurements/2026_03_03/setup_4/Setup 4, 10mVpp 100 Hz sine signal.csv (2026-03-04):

Sample | Voltage (mV)
0 | -8.06025887
1 | -8.08546925
2 | -8.15374851
3 | -8.1676054
4 | -8.1759882
5 | -8.17918301
6 | -8.18150806
7 | -8.17893696
8 | -8.20640564
9 | -8.27510929
10 | -8.2567606
11 | -8.20620441
12 | -8.15830803
13 | -8.14619446
14 | -8.12337589
15 | -8.08598423
16 | -8.06327629
17 | -8.0474968
18 | -8.09689045
19 | -8.13034821
20 | -8.12565517
21 | -8.12514114
22 | -8.12431431
23 | -8.12818146
24 | -8.13522053
25 | -8.20593643
26 | -8.2496748
27 | -8.22106743
28 | -8.16011906
29 | -8.12507439
30 | -8.10844517
31 | -8.07641792
32 | -8.04959774
33 | -8.03670216
34 | -8.05174351
35 | -8.1276226
36 | -8.14554691
37 | -8.14664173
38 | -8.14420509
39 | -8.14214897
40 | -8.1453228
41 | -8.16972923
42 | -8.26145363
43 | -8.26791286
44 | -8.2334938
45 | -8.18009949
46 | -8.1627121
47 | -8.14094162
48 | -8.10167408
49 | -8.07744598
50 | -8.06182384
51 | -8.10553932
52 | -8.16849995
53 | -8.17735004
54 | -8.18204403
55 | -8.18691635
56 | -8.19292831
57 | -8.19085026
58 | -8.23409748
59 | -8.29138088
60 | -8.26755524
61 | -8.21275234
62 | -8.17305946
63 | -8.16291332
64 | -8.1361599
65 | -8.10118198
66 | -8.07880974
67 | -8.06591415
68 | -8.12100601
69 | -8.14391518
70 | -8.14138889
71 | -8.14409351
72 | -8.14416027
73 | -8.14740181
74 | -8.16255569
75 | -8.24189758
76 | -8.26489544
77 | -8.22701168
78 | -8.15701199
79 | -8.12147522
80 | -8.09838772
81 | -8.0587616
82 | -8.02928257
83 | -8.01692295
84 | -8.04535103
85 | -8.11606693
86 | -8.12500763
87 | -8.12431431
88 | -8.12417984
89 | -8.12536526
90 | -8.12844849
91 | -8.16447639
92 | -8.25074768
93 | -8.24449062
94 | -8.20691967
95 | -8.15862179
96 | -8.14089775
97 | -8.11597824
98 | -8.07543468
99 | -8.04950809
100 | -8.03457832
101 | -8.085783
102 | -8.13426018
103 | -8.14190292
104 | -8.14601612
105 | -8.15140247
106 | -8.15564823
107 | -8.13504219
108 | -8.12145329
109 | -8.09671211
110 | -8.07062912
111 | -8.0579567
112 | -8.06379032
113 | -8.13620472
114 | -8.16175079
115 | -8.16018581
116 | -8.16099072
117 | -8.15801811
118 | -8.15707874
119 | -8.17008686
120 | -8.25517368
121 | -8.2770319
122 | -8.24757481
123 | -8.18709564
124 | -8.16400814
125 | -8.14588165
126 | -8.1071043
127 | -8.07990551

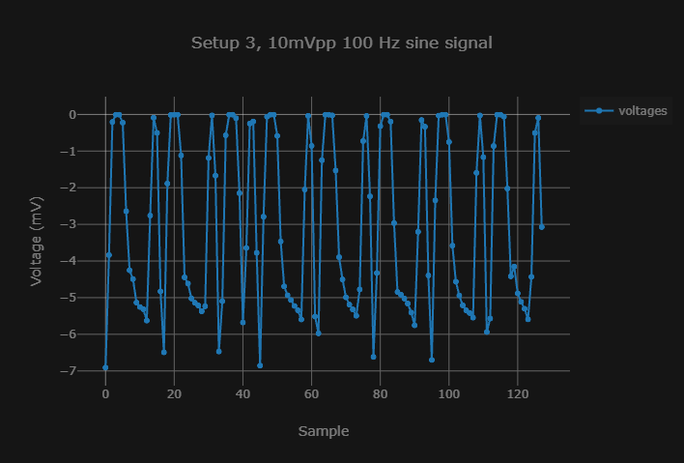
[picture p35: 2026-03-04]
notes/emg recording/measurements/2026_03_03/setup_3/Setup 3, 10mVpp 100 Hz sine signal.png

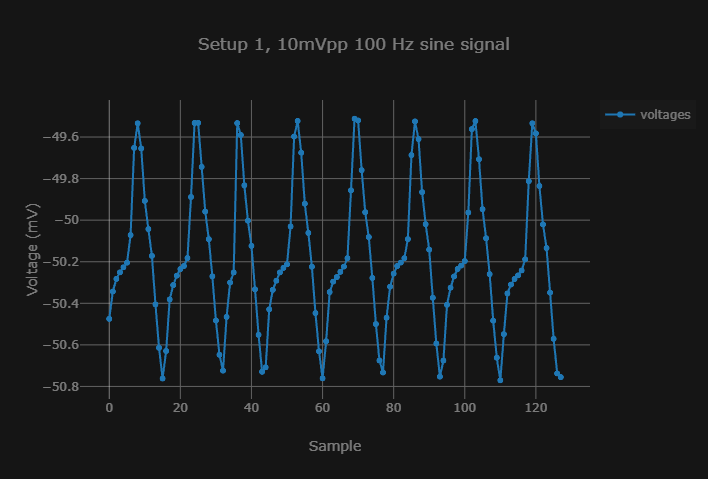
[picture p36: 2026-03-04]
notes/emg recording/measurements/2026_03_03/setup_1/Setup 1, 10mVpp 100 Hz sine signal.png

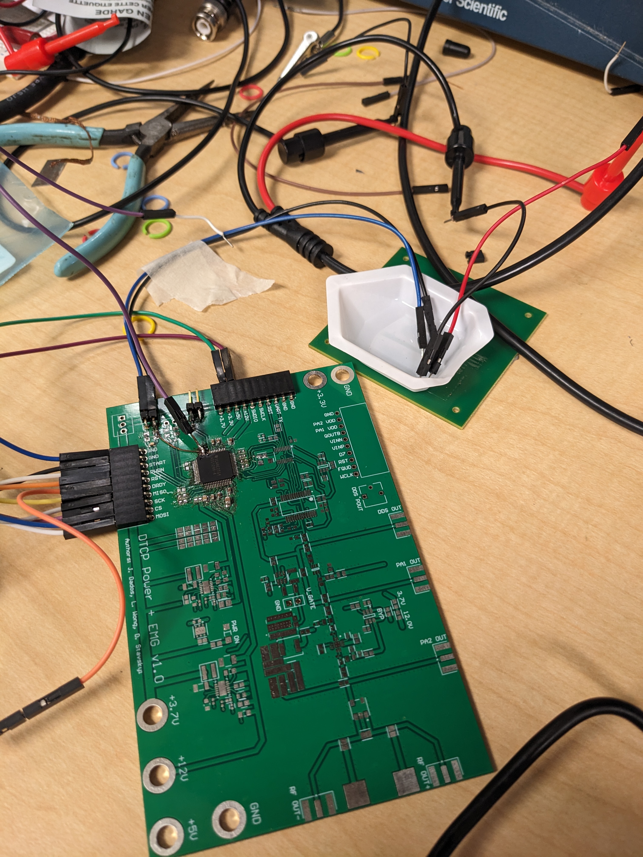
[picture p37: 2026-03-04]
notes/emg recording/measurements/2026_03_03/setup_2/setup_2.jpg

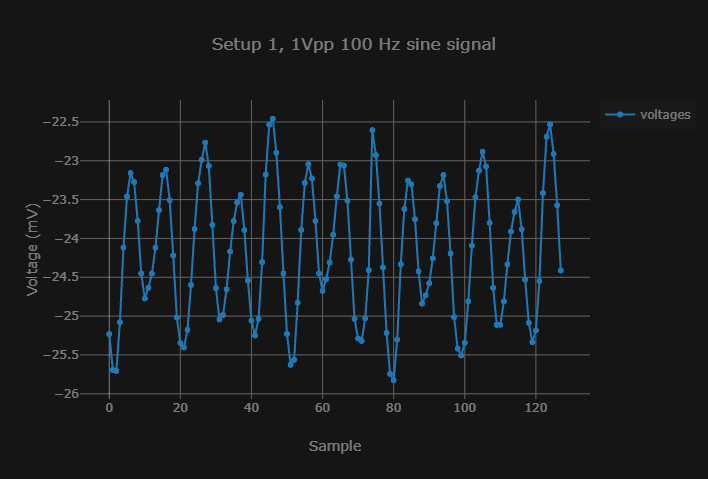
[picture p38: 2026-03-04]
notes/emg recording/measurements/2026_03_03/setup_1/Setup 1, 1Vpp 100 Hz sine signal.png

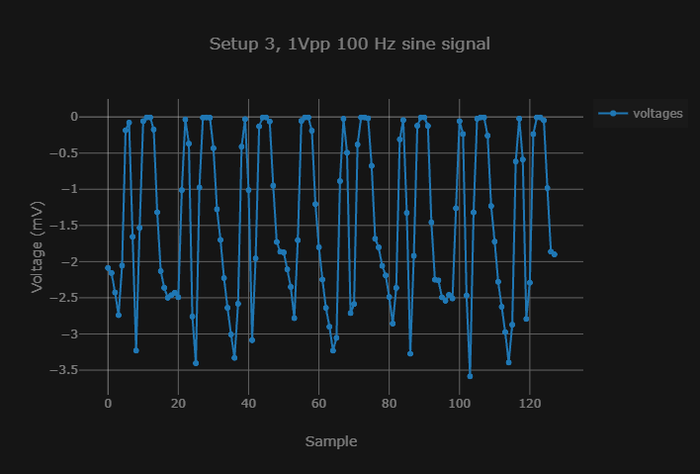
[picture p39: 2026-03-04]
notes/emg recording/measurements/2026_03_03/setup_3/Setup 3, 1Vpp 100 Hz sine signal.png

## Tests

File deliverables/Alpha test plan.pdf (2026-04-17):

## Alpha test plan

Jeremiah Dados, Dmytro Stavskyi, and Luis Wong

1. Target performance metrics

The goal of testing the alpha version of the device will be to determine if the target values for key specifications can be met with our circuit designs.

Performance metric | Target value | Explanation
Output frequency | 25 MHz | Measured with an RF spectrum analyzer.
Output power | ≥30 dBm differential | Measured with an RF spectrum analyzer. 30 dBm differential = 27 dBm per electrode.
Static current | <10 mA | Current consumed when the RF signal is not being transmitted. Needed for 12 hr battery life with a 140 mAh battery.
Tx current | <500 mA | Current consumed when the RF signal is being transmitted.
EMG noise floor | <0.5 mV | EMG spikes reach up to +5 mV, which would give us an SNR of 10 dB.
EMG sampling rate | ≥1000 samples/s | Enough to measure signals up to 500 Hz.
2. MCU circuit validation
a. Expected behavior
After assembling the microcontroller circuit and making the connections to the programmer/debugger, the device is recognized by the CCS IDE, and it can be flashed with firmware.
b. Test procedure
Set up the devices as follows:

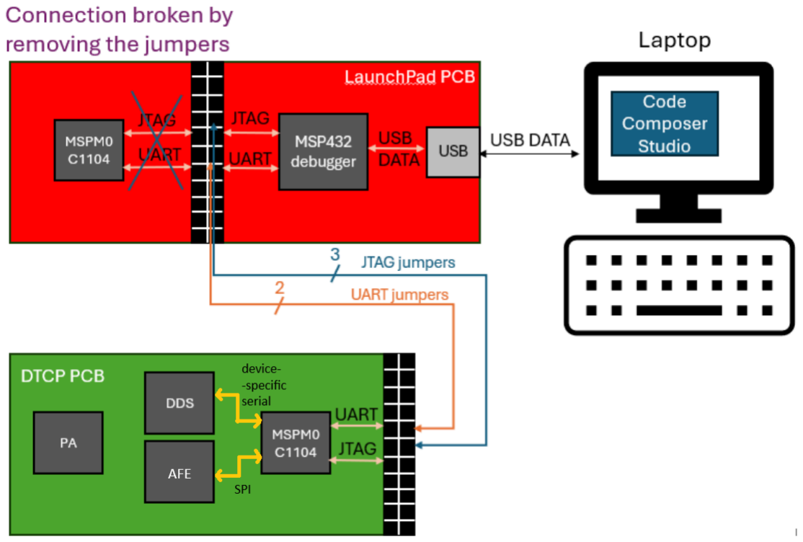
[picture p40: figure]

Connect the TMS, TCK, and RST lines from the Launchpad to the corresponding pins on the PCB. Connect 3.3V power from a DC power supply to the corresponding power port on the PCB. Open CCS on the laptop connected to the Launchpad, then click “Debug project” on any firmware project and observe if the debugging launches correctly and the code execution can be paused and continued.

3. RF circuit validation
a. Expected behavior

For the class-A PA circuit:
- DDS output: 0 ~ 10 dBm @ 25 MHz
- PA1 output: 5 ~ 15 dBm @ 25 MHz
- PA2 output: 30 ~ 33 dBm @ 25 MHz
For the class-E PA circuit
- 3.3 Vpp 25 MHz square wave at the DDS output
- 5 Vpp 25 MHz square wave at the PA1 (Gate Driver) output
- 30 - 35 dBm @ 25 MHz at the PA2 output
b. Test procedure

Set up equipment as follows:

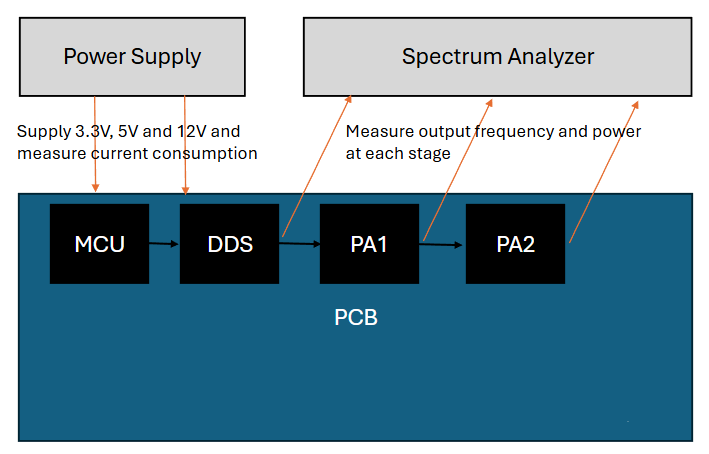
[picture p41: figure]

Measure outputs in the order of the signal chain: DDS, then PA1, then PA2. Test each stage by powering it with a DC power supply, taking note of the initial static current. Then activate the DDS output and take note of the PA output power and frequency.

4. Power circuit validation
a. Expected behavior
The LDO and two buck converters output within 0.05V of the target output voltage.
b. Test procedure
Set up the equipment as follows:

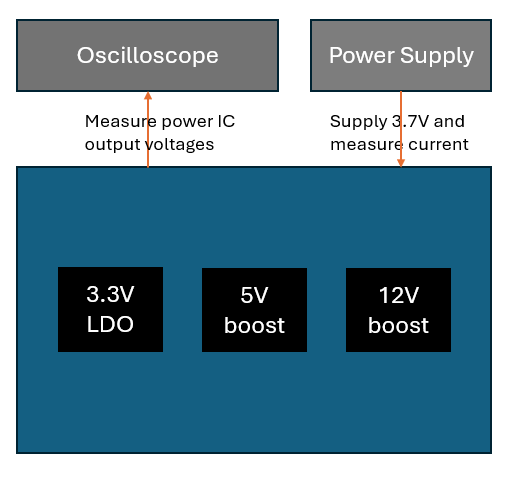
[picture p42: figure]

Use a DC power supply in place of the 3.7V battery, and measure the LDO and boost converters’ output voltages with an oscilloscope.

5. EMG recording validation
a. Expected behavior
The AFE responds to SPI commands, returning correct values in accordance with the datasheet. The SPI waveforms investigated with an oscilloscope are in line with the timing diagrams from the datasheet.
The measured voltage values recreate the waveform and the amplitude of the channel input and signal-to-noise (SNR) ratio is 10 dB or higher, meaning that the noise floor is below 0.5 mV.
Data ready signal is asserted at the rate of ~ 1 kHz (equivalent to the sampling rate)
b. Test procedure

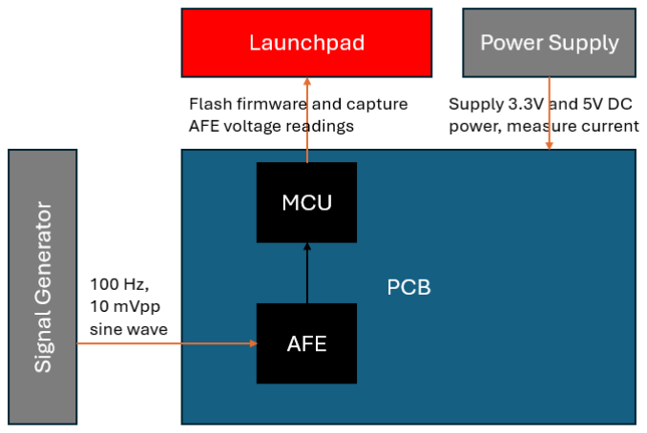
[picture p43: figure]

Use power supply to supply 3.3V and 5V DC for the digital and analog parts of the board. Use a function generator to supply a 100 Hz, 10 mVpp sine wave to the input of a channel. Debug the firmware project using CCS and use the Graph functionality to continuously plot the recorded values. Short the inputs of the channel and record the channel data to measure the noise. Use the oscilloscope to measure the SPI signals and the frequency of the falling edge of the data ready signal.

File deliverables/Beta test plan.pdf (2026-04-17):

## Beta test plan

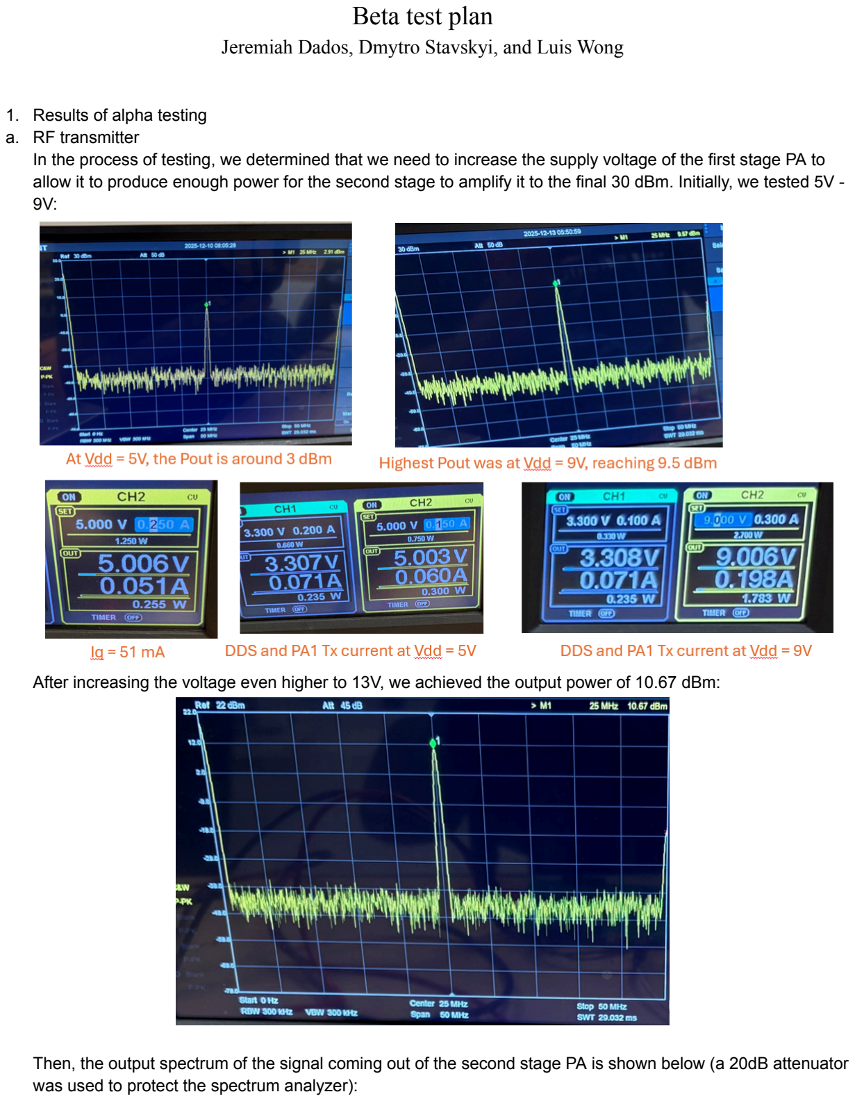
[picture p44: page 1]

Jeremiah Dados, Dmytro Stavskyi, and Luis Wong

1. Results of alpha testing
a. RF transmitter
In the process of testing, we determined that we need to increase the supply voltage of the first stage PA to allow it to produce enough power for the second stage to amplify it to the final 30 dBm. Initially, we tested 5V -9V:

After increasing the voltage even higher to 13V, we achieved the output power of 10.67 dBm:

Then, the output spectrum of the signal coming out of the second stage PA is shown below (a 20dB attenuator was used to protect the spectrum analyzer):

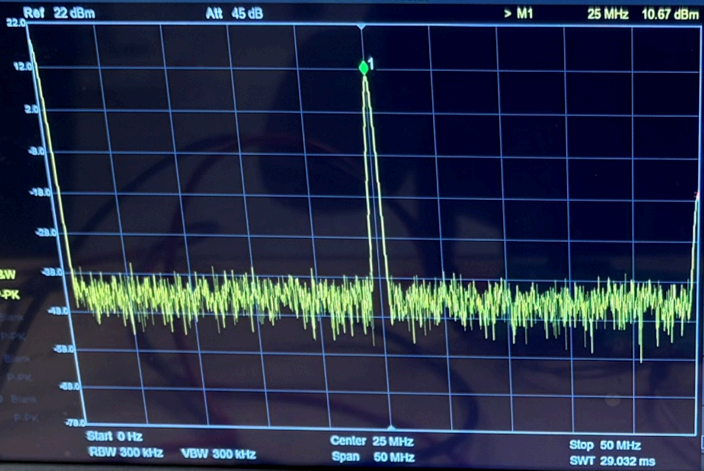
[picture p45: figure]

As we can see, the output power is 30.67 dBm (after adding the 20 dB absorbed by the attenuator).
During transmission, the current consumption is 100 mA for the 3.3V supply and 330 mA for the 13V supply:

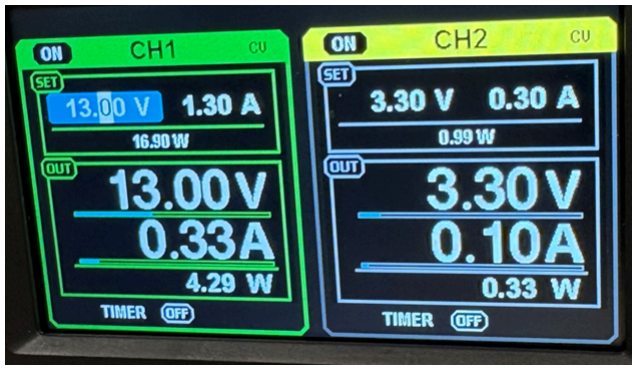
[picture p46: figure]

When the device is not transmitting power, the idle current is below 10 mA thanks to the use of power switches that disable the DDS and power amplifiers.

b. EMG recording system
In the process of testing, we realized that the AFE chips needs +2.5V DC bias applied to the inputs to be able to record the signals. We had to manually solder a wire to the AFE bias pins and then connect it to the negative analog input:

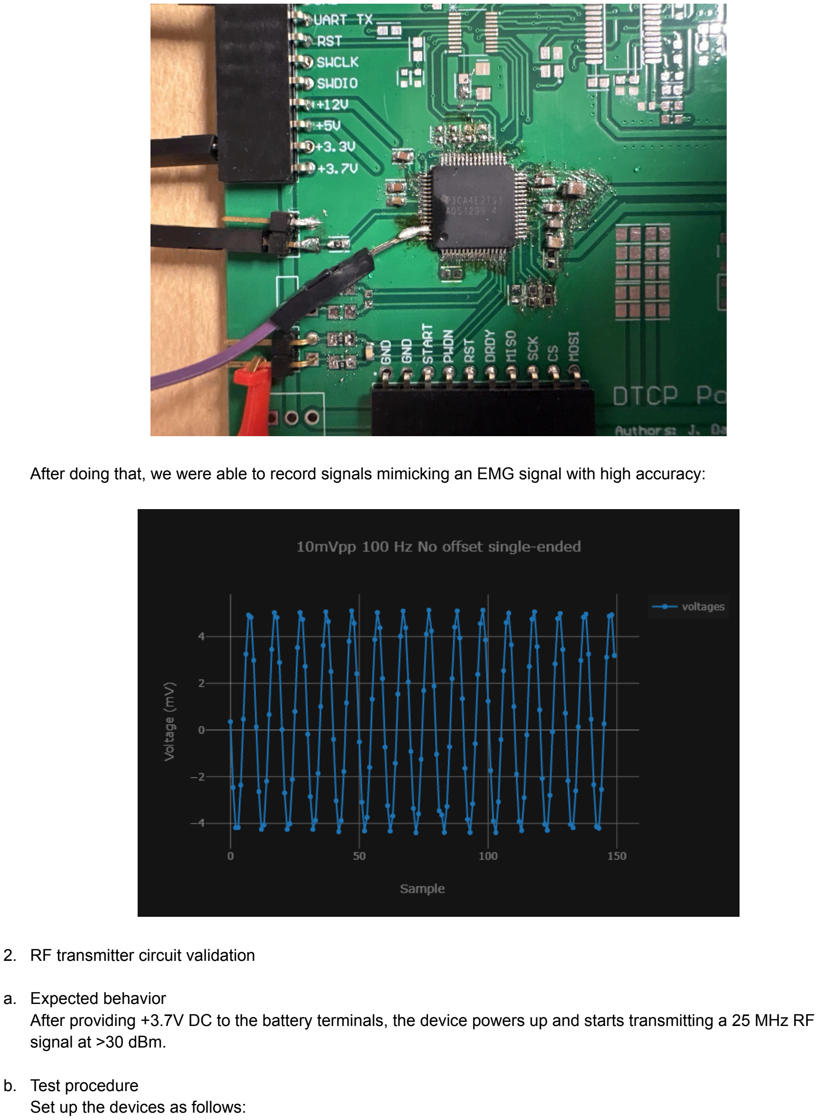
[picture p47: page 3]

After doing that, we were able to record signals mimicking an EMG signal with high accuracy:

2. RF transmitter circuit validation
a. Expected behavior
After providing +3.7V DC to the battery terminals, the device powers up and starts transmitting a 25 MHz RF signal at >30 dBm.
b. Test procedure
Set up the devices as follows:

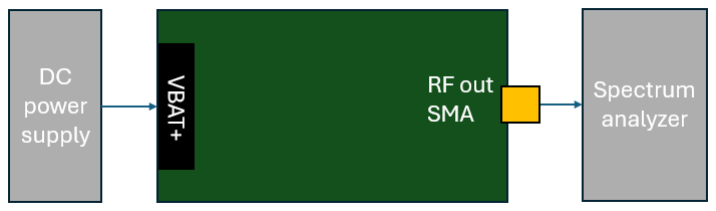
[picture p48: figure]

The goal is to only provide DC power emulating a battery, let the device handle all internal signals and see it output the target signal (25 MHz at 30+ dBm).

3. EMG recording validation
a. Expected behavior

The AFE should be able to read an AC signal in saline medium with an SNR of at least 10 dB (e.g noise floor of 0.5 mV for 5mV EMG signals) to emulate recording a real muscle.

b. Test procedure

Use a power supply to supply 3.3V and 5V DC for the digital and analog parts of the board. Use a function generator to supply a 100 Hz, 10 mVpp sine wave to the input of a channel through the saline medium. Debug the firmware project using CCS and use the Graph functionality to continuously plot the recorded values.

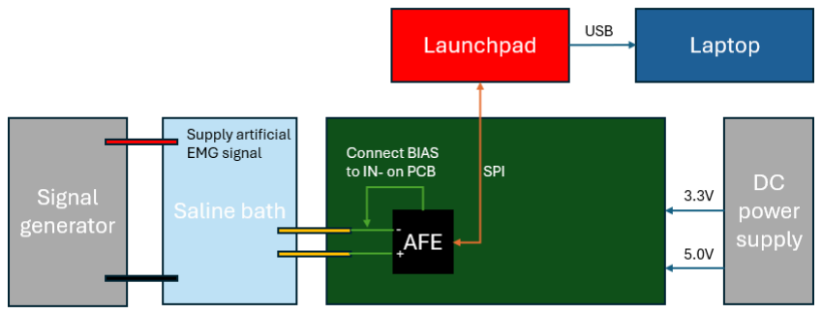
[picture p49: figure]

The goal is to obtain a graph of an artificial EMG signal on the laptop connected to the AFE via a Launchpad.

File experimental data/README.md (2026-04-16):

# Experimental Data

Some pictures of EMG plot recorded by our hardware. May add other things later.

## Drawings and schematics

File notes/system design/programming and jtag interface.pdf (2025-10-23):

## Connection broken by removing the jumpers

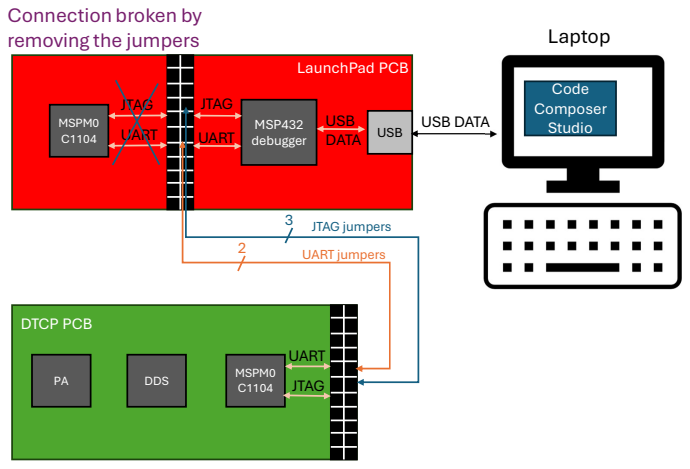
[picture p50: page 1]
MSP432 debugger; MSPM0; USB; JTAG; UART; USB DATA; DDS; UART jumpers; JTAG jumpers; LaunchPad PCB; DTCP PCB; UART JTAG; Code Composer Studio; Laptop

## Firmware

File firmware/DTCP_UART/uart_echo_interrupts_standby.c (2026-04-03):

/*
 * Copyright (c) 2020, Texas Instruments Incorporated
 * All rights reserved.
 *
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
 * *  Redistributions of source code must retain the above copyright
 *    notice, this list of conditions and the following disclaimer.
 *
 * *  Redistributions in binary form must reproduce the above copyright
 *    notice, this list of conditions and the following disclaimer in the
 *    documentation and/or other materials provided with the distribution.
 *
 * *  Neither the name of Texas Instruments Incorporated nor the names of
 *    its contributors may be used to endorse or promote products derived
 *    from this software without specific prior written permission.
 *
 * THIS SOFTWARE IS PROVIDED BY THE COPYRIGHT HOLDERS AND CONTRIBUTORS "AS IS"
 * AND ANY EXPRESS OR IMPLIED WARRANTIES, INCLUDING, BUT NOT LIMITED TO,
 * THE IMPLIED WARRANTIES OF MERCHANTABILITY AND FITNESS FOR A PARTICULAR
 * PURPOSE ARE DISCLAIMED. IN NO EVENT SHALL THE COPYRIGHT OWNER OR
 * CONTRIBUTORS BE LIABLE FOR ANY DIRECT, INDIRECT, INCIDENTAL, SPECIAL,
 * EXEMPLARY, OR CONSEQUENTIAL DAMAGES (INCLUDING, BUT NOT LIMITED TO,
 * PROCUREMENT OF SUBSTITUTE GOODS OR SERVICES; LOSS OF USE, DATA, OR PROFITS;
 * OR BUSINESS INTERRUPTION) HOWEVER CAUSED AND ON ANY THEORY OF LIABILITY,
 * WHETHER IN CONTRACT, STRICT LIABILITY, OR TORT (INCLUDING NEGLIGENCE OR
 * OTHERWISE) ARISING IN ANY WAY OUT OF THE USE OF THIS SOFTWARE,
 * EVEN IF ADVISED OF THE POSSIBILITY OF SUCH DAMAGE.
 */

#include <stdio.h>
#include "ti_msp_dl_config.h"

// Array of floats
float dataArray[] = {0.0000, 0.7347, 1.1888, 1.1888, 0.7347, 0.0000, -0.7347, -1.1888, -1.1888, -0.7347, -0.0000, 0.7347, 1.1888, 1.1888, 0.7347, 0.0000, -0.7347, -1.1888, -1.1888, -0.7347, -0.0000, 0.7347, 1.1888, 1.1888, 0.7347, -0.0000, -0.7347, -1.1888, -1.1888, -0.7347, -0.0000, 0.7347, 1.1888, 1.1888, 0.7347, -0.0000, -0.7347, -1.1888, -1.1888, -0.7347, -0.0000, 0.7347, 1.1888, 1.1888, 0.7347, 0.0000, -0.7347, -1.1888, -1.1888, -0.7347, 0.0000, 0.7347, 1.1888, 1.1888, 0.7347, -0.0000, -0.7347, -1.1888, -1.1888, -0.7347, 0.0000, 0.7347, 1.1888, 1.1888, 0.7347, -0.0000, -0.7347, -1.1888, -1.1888, -0.7347, 0.0000, 0.7347, 1.1888, 1.1888, 0.7347, -0.0000, -0.7347, -1.1888, -1.1888, -0.7347, -0.0000, 0.7347, 1.1888, 1.1888, 0.7347, -0.0000, -0.7347, -1.1888, -1.1888, -0.7347, 0.0000, 0.7347, 1.1888, 1.1888, 0.7347, -0.0000, -0.7347, -1.1888, -1.1888, -0.7347}; 

#define ARRAY_SIZE (sizeof(dataArray) / sizeof(dataArray[0]))

volatile uint8_t gCurrentIndex = 0; // Tracks which element to send next
volatile uint8_t gTxState = 0; // 0: Header, 1-4: Float Bytes
const uint8_t HEADER_BYTE = 0xAA;

void UART_transmitString(char* str) {
    while (*str) {
        // Wait for TX FIFO to have space, then send
        DL_UART_Main_transmitDataBlocking(UART_0_INST, *str++);
    }
}

// void transmitFloatArray() {
//     char buffer[32];
//     for (int i = 0; i < ARRAY_SIZE; i++) {
//         float val = dataArray[i];
        
//         // Handle negative numbers
//         if (val < 0) {
//             UART_transmitString("-");
//             val = -val;
//         }

//         int intPart = (int)val;
//         int fracPart = (int)((val - intPart) * 100); // 2 decimal places

//         // Format into buffer: "12.34\r\n"
//         sprintf(buffer, "%d.%02d\r\n", intPart, fracPart);
//         UART_transmitString(buffer);
//     }
// }

// void transmitFloatArrayPlotter() {
//     char buffer[32];
//     for (int i = 0; i < ARRAY_SIZE; i++) {
//         float val = dataArray[i];
        
//         // Manual float formatting
//         int intPart = (int)val;
//         int fracPart = (int)((val - (float)intPart) * 100.0f);
//         if (fracPart < 0) fracPart = -fracPart; // Ensure decimal is positive

//         // Format: "Value," for first elements, "Value\r\n" for the last one
//         // if (i < ARRAY_SIZE - 1) {
//         //     snprintf(buffer, sizeof(buffer), "%d.%02d,", intPart, fracPart);
//         // } else {
//         //     snprintf(buffer, sizeof(buffer), "%d.%02d\r\n", intPart, fracPart);
//         // }

//         snprintf(buffer, sizeof(buffer), "%d.%02d\r\n", intPart, fracPart);
        
//         UART_transmitString(buffer);
//     }
// }

// void transmitNextValue() {
//     char buffer[32];
//     float val = dataArray[gCurrentIndex];

//     // Manual float to string conversion
//     int intPart = (int)val;
//     int fracPart = (int)((val - (float)intPart) * 100.0f);
//     if (fracPart < 0) fracPart = -fracPart; 

//     // Serial Plotter needs one value + newline to plot a single point
//     snprintf(buffer, sizeof(buffer), "%d.%02d\r\n", intPart, fracPart);
//     UART_transmitString(buffer);

//     // Increment index and wrap around to the start of the array
//     gCurrentIndex++;
//     if (gCurrentIndex >= ARRAY_SIZE) {
//         gCurrentIndex = 0;
//     }
// }

void transmitFloat(float val) {
    // 1. Handle negative sign
    if (val < 0) {
        DL_UART_Main_transmitDataBlocking(UART_0_INST, '-');
        val = -val;
    }

    // 2. Transmit integer part
    int intPart = (int)val;
    DL_UART_Main_transmitDataBlocking(UART_0_INST, (intPart + '0'));

    // 3. Transmit decimal point
    DL_UART_Main_transmitDataBlocking(UART_0_INST, '.');

    // 4. Transmit fractional part (2 decimal places)
    int fracPart = (int)((val - (float)intPart) * 100.0f + 0.5f); // +0.5 for rounding
    DL_UART_Main_transmitDataBlocking(UART_0_INST, (fracPart / 10) + '0');
    DL_UART_Main_transmitDataBlocking(UART_0_INST, (fracPart % 10) + '0');

    // 5. Newline for Plotter
    DL_UART_Main_transmitDataBlocking(UART_0_INST, '\r');
    DL_UART_Main_transmitDataBlocking(UART_0_INST, '\n');
}

void transmitFloatBinary(float val) {
    // 1. Create a pointer to the float and treat it as a byte array
    uint8_t *ptr = (uint8_t *)&val;

    // 2. Send Frame Start (many tools use 0xABCD or 0xAA)
    DL_UART_Main_transmitDataBlocking(UART_0_INST, 0xAA); 

    // 3. Transmit each of the 4 bytes in the float
    for (int i = 0; i < sizeof(float); i++) {
        // DL_UART_Main_transmitDataBlocking sends 1 byte at a time
        DL_UART_Main_transmitDataBlocking(UART_0_INST, ptr[i]);
    }
}

// Update your loop to use this:
void transmitNextValue() {
    transmitFloatBinary(dataArray[gCurrentIndex]);
    gCurrentIndex = (gCurrentIndex + 1) % ARRAY_SIZE;
}

volatile uint8_t byteCount = 1; // Start at 1 because we manually sent byte 0

void UART_0_INST_IRQHandler(void) {
    switch (DL_UART_Main_getPendingInterrupt(UART_0_INST)) {
        case DL_UART_MAIN_IIDX_TX:
            
            float val = dataArray[gCurrentIndex];
            uint8_t *ptr = (uint8_t *)&val;

            if (gTxState == 0) {
                // State 0: Send Header
                DL_UART_Main_transmitData(UART_0_INST, HEADER_BYTE);
                gTxState = 1;
            } 
            else if (gTxState <= 4) {
                // State 1-4: Send the 4 bytes of the float
                // ptr[0] for state 1, ptr[1] for state 2, etc.
                DL_UART_Main_transmitData(UART_0_INST, ptr[gTxState - 1]);
                gTxState++;
                
                // If we just sent the last byte (state 4), reset for the next float
                if (gTxState > 4) {
                    gTxState = 0;
                    gCurrentIndex = (gCurrentIndex + 1) % ARRAY_SIZE;
                }
            }
            break;
            
        default:
            break;
    }
}

int main(void) {
    SYSCFG_DL_init();

    // Enable UART Interrupts in NVIC
    NVIC_EnableIRQ(UART_0_INST_INT_IRQN);

    // START: Manually send the very first header to kick off the ISR
    DL_UART_Main_transmitData(UART_0_INST, HEADER_BYTE);
    gTxState = 1; // Next interrupt should send the first byte of the float
    
    // Transmit the whole array once
    // transmitFloatArray();

    while (1) {
        // transmitFloatArrayPlotter(); // Plot the array repeatedly
        // transmitNextValue(); 

        // DL_Common_delayCycles(32000000); // Delay to plotter does not move too fast.
        __WFI();
    }
}

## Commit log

2025-10-24 Found a good power switch
2025-10-28 Incomplete Altium schematic of the EMG recording circuit
    [ADS1299.SchDoc]
2025-10-28 Preliminary MCU schematic
    [MCU.SchDoc]
2025-10-28 moved file to schematics
    [ADS1299.SchDoc]
2025-10-28 Upload basic PA implementation schemtic.
    [PowerAmp.SchDoc]
2025-10-28 updated the schematic for the EMG recording system
    [ADS1299.SchDoc]
2025-11-01 Attempt to simulate PA with 10V Driver.
2025-11-01 Added the Altium PCB project
    [878311411.PcbLib, 878311411.SchLib, AFE.SchDoc, Bill of Materials-Tx_Electrode_PA_Power.xlsx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]
2025-11-01 Added square wave functonality to DDS
    [DDS.SchDoc, PA stage 1.SchDoc]
2025-11-01 Added gate driver to PA stage 1
    [DDS.SchDoc, DTCP v1.2.PrjPcb, PA stage 1.SchDoc, System.SchDoc]
2025-11-01 Updated the reference voltages and added a note about extrernal / internal clock
    [AFE.SchDoc]
2025-11-01 Added initial class-E PA design
    [PA stage 2.SchDoc]
2025-11-01 Updaded AFE schematic (as test)
    [AFE.SchDoc]
2025-11-02 Modified PA stage 2 to include Class E amplfier.
    [PA stage 2.SchDoc]
2025-11-03 Layout progress
    [AFE.SchDoc, PA stage 1.SchDoc, PA stage 2.SchDoc, System.SchDoc]
2025-11-03 Added one power net with zero ohm resistors to select between 12 and 5 V to stages 1 and 2
    [PA stage 2.SchDoc]
2025-11-03 Finished the schematic design.
    [PA stage 1.SchDoc, PA stage 2.SchDoc, System.SchDoc]
2025-11-03 Updated annotation
    [DTCP v1.2.PrjPcb, PA stage 2.SchDoc, System.SchDoc]
2025-11-03 Added 5V boost converter
    [Boost 5V.SchDoc, DDS.SchDoc, PA stage 1.SchDoc, System.SchDoc]
2025-11-04 Fixed RF inductor in the PMA PA
    [Boost 5V.SchDoc, DDS.SchDoc, PA stage 2.SchDoc, System.SchDoc]
2025-11-04 Continuing PCB work.
    [AFE.SchDoc, DDS.SchDoc, PA stage 2.SchDoc, Switch1.SchDoc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]
2025-11-04 Fixed the AFE schematic
    [AFE.SchDoc, MCU.SchDoc, System.SchDoc]
2025-11-04 Fixed schematic errors
    [AFE.SchDoc, Boost 12V.SchDoc, Boost 5V.SchDoc, DDS.SchDoc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]
2025-11-04 Basic layout 90% complete
    [Boost 12V.SchDoc, Boost 5V.SchDoc, DTCP v1.2.PrjPcb, LDO.SchDoc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]
2025-11-04 Added the LEDs and the ground electrode
    [AFE.SchDoc, DDS.SchDoc, MCU.SchDoc, PA stage 1.SchDoc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]
2025-11-04 Layout 80% done
    [MCU.SchDoc, System.SchDoc]
2025-11-05 Routing connectors
2025-11-05 Layout done except for polygons.
    [AFE.SchDoc, DTCP v1.2.PrjPcb, PA stage 2.SchDoc, System.SchDoc]
2025-11-06 Layout v1.0 complete
    [DTCP v1.2.PrjPcb, Output.SchDoc, System.SchDoc]
2025-11-07 Small changes to the schematic to further de-risk.
    [AFE.SchDoc, Boost 12V.SchDoc, Boost 5V.SchDoc, DTCP v1.2.PrjPcb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]
2025-11-08 Layout complete
    [AFE.SchDoc, Boost 12V.SchDoc, Boost 5V.SchDoc, DTCP v1.2.PrjPcb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]
2025-11-08 Added board outline
    [AFE.SchDoc, Bill of Materials-DTCP v1.2.xlsx, Boost 12V.SchDoc, Boost 5V.SchDoc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]
2025-11-08 More debug option in schematic
    [PA stage 1.SchDoc, System.SchDoc]
2025-11-08 GaN layout
    [System.SchDoc]
2025-11-08 Added connection to gate for GaN class-E
    [System.SchDoc]
2025-11-10 Generated fabrication outputs
    [AFE.SchDoc, Bill of Materials-DTCP v1.2.xlsx, Boost 12V.SchDoc, Boost 5V.SchDoc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]
2025-11-10 Small layout updates
    [PA stage 2.SchDoc]
2025-11-12 Small layout changes requested by Han
    [Bill of Materials-DTCP v1.2.xlsx, PA stage 2.SchDoc, PCB1.GBL, PCB1.GBO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]
2025-11-17 Made changes to README to include current bugs.
2025-11-17 Toggles the Red LED (LED1) on board
2025-11-30 Can print a string with UART now
2025-12-01 Included the pins currently used on the board for SPI
2026-01-25 Progress with the firmware; Data Ready signal is asserted when the start pin is pulled high
2026-01-27 Added known bugs for the EMG circuit
2026-01-30 Added simple code to demonstrate power switching.
2026-01-30 LTspice files for simulating Class E circuit on our board.
2026-01-30 Update Class A PA section in README
    Expanded explanation of issues with Class A PA gain and power regulation.
2026-02-08 Can measure a differential normal input signal with a 2.5V offset
2026-02-08 Deleted unnecessary history files, set up the Altium project for the next PCB version.
    [878311411.PcbLib, 878311411.SchLib, AFE.SchDoc, Bill of Materials-DTCP v1.2.xlsx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]
2026-02-08 Schematic revisions to the MCU.
    [MCU.SchDoc]
2026-02-08 Revisions to the DDS circuit
    [DDS.SchDoc]
2026-02-08 Revisions to the boost converter circuit
    [Boost 12V.SchDoc, DDS.SchDoc]
2026-02-08 Revisions to the first stage PA circuit
    [Boost 12V.SchDoc, PA stage 1.SchDoc, System.SchDoc]
2026-02-08 Revisions to the second stage PA circuit
    [PA stage 1.SchDoc, PA stage 2.SchDoc]
2026-02-08 Updates to the 5V boost converter circuit.
    [Boost 5V.SchDoc, PA stage 2.SchDoc]
2026-02-08 Updates to the system schematic.
    [Boost 12V.SchDoc, Boost 5V.SchDoc, DDS.SchDoc, PA stage 1.SchDoc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]
2026-02-08 Started work on the PCB layout
    [PCB1.PcbDoc]
2026-02-08 Can measure a 10mVpp 100 Hz sine wave single-ended with a 2.5 offset
2026-02-09 Updated bugs for the firmware and the AFE circuit
2026-02-10 Making the layout more compact
    [PCB1.PcbDoc]
2026-02-11 Making PCB more compact
    [PCB1.PcbDoc]
2026-02-17 Making the design more compact
    [PCB1.PcbDoc, System.SchDoc]
2026-02-17 Making the PCB more compact.
    [PCB1.PcbDoc]
2026-02-18 Making the PCB more compact
    [PCB1.PcbDoc]
2026-02-18 Updates to AFE schematic to include bias circuits
    [AFE.SchDoc]
2026-02-18 General shape of the layout complete
    [PCB1.PcbDoc, System.SchDoc]
2026-02-18 Lab work updates.
    [PCB1.PcbDoc]
2026-02-20 Verified that the power switch for the PAs works
2026-02-21 Continuing work on PCB
    [PCB1.PcbDoc, System.SchDoc]
2026-02-23 Continuing PCB work
    [PCB1.PcbDoc]
2026-02-24 Continuing work on the layout
    [PCB1.PcbDoc]
2026-02-25 Added an RC filter between BIASOUT and BIASINV
    [AFE.SchDoc, PCB1.PcbDoc]
2026-02-26 Layout 95% finished.
    [AFE.SchDoc, DTCP v2.0.PrjPcb, PCB1.PcbDoc]
2026-03-01 Added pulsed powering to the TX firmware
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2026-03-01 DRC pass
    [PCB1.PcbDoc]
2026-03-02 Removed RESET, PWDN, and START pins since those can be executed as commands with SPI.
    [AFE.SchDoc, MCU.SchDoc, System.SchDoc]
2026-03-02 Note for MCU SPI pins
    [MCU.SchDoc]
2026-03-03 Fixed POCI pin assignment in the MCU schematic.
    [MCU.SchDoc]
2026-03-03 Moved DDS_EN from PA0 (open drain) to PA2 (regular). Added UART Rx available through header.
    [MCU.SchDoc, System.SchDoc]
2026-03-03 AFE measurement with saline for 3rd March
    [Setup 1, 10mVpp 100 Hz sine signal.csv, Setup 1, 1Vpp 100 Hz sine signal.csv, Setup 1, 2.5Vpp 100 Hz sine signal.csv, Setup 2, 10mVpp 100 Hz sine signal.csv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]
2026-03-04 Added a missing library to the Altium project
    [AFE.SchDoc, Bill of Materials-DTCP v1.2.xlsx, Boost 12V.SchDoc, Boost 5V.SchDoc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]
2026-03-04 Fixed footprint in AFE schematic
    [AFE.SchDoc]
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2026-03-04 fix to csv files to properly process the data
    [Setup 1, 10mVpp 100 Hz sine signal.csv, Setup 1, 1Vpp 100 Hz sine signal.csv, Setup 1, 2.5Vpp 100 Hz sine signal.csv, Setup 2, 10mVpp 100 Hz sine signal.csv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]
2026-03-04 Layout and schematic fixes
    [AFE.SchDoc, DDS.SchDoc, MCU.SchDoc, PCB1.PcbDoc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]
2026-03-04 Fixing the MCU pin assignments, making AFE schematic more flexible
    [AFE.SchDoc, PCB1.PcbDoc, System.SchDoc]
2026-03-04 Pass DRC
    [PCB1.PcbDoc]
2026-03-04 Fabrication outputs
    [AFE.SchDoc, Bill of Materials-DTCP v2.0.xlsx, Boost 12V.SchDoc, Boost 5V.SchDoc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]
2026-03-04 Some small fixes
    [DTCP elecrow BOM.xlsx, Output.SchDoc, PCB1.PcbDoc, System.SchDoc]
2026-03-04 Updated fabrication outputs
    [Bill of Materials-DTCP v2.0.xlsx, Output.SchDoc, PCB1.GBL, PCB1.GBO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]
2026-03-05 Added 0ohm resistors at SPI lines
    [AFE.SchDoc, PCB1.GBL, PCB1.GBO, PCB1.GBP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]
2026-03-05 Layout updates
    [AFE.SchDoc, DTCP v2.0.PrjPcb, MCU.SchDoc, PCB1.PcbDoc]
2026-03-05 missing library added
    [ADS1299-4PAGR.SchLib, DTCP v2.0.PrjPcb, QFP50P1200X1200X120-64N.PcbLib]
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2026-03-24 Added a script to generate the EMG signal with an artifact based on Han's data. Generated the CSV of the signal.
    [emg_artifact_waveform.csv]
2026-03-24 Added code to generate the control signal (no EMG, only stimulation spike)
    [emg.csv, emg_control_waveform.csv, emg_ctrl.csv]
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2026-03-31 Added header frame byte to fix with UART synchronization when receiving the data
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2026-04-05 Schematic fixes
    [Boost 12V.SchDoc, Boost 5V.SchDoc, PA stage 1.SchDoc, PA stage 2.SchDoc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]
2026-04-05 More fixes and updated layout
    [AFE.SchDoc, Boost 5V.SchDoc, Output.SchDoc, PA stage 1.SchDoc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]
2026-04-05 Date ready signal is asserted but measurements are incorrect and reading registers also yields incorrect values that change every time. This implies timing issue but not sure if it a firmware issue a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
2026-04-12 Cleaned up schematics
    [AFE.SchDoc, Boost 5V.SchDoc, DDS.SchDoc, MCU.SchDoc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]
2026-04-13 Fixed EMG electrode silkscreen markings.
    [AFE.SchDoc, PCB1.PcbDoc]
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
